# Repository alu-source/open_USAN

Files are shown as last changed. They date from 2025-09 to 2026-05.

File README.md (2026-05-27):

## Summary

1. Overview
2. Build instructions
3. Testing and validation 

## 1. Overview
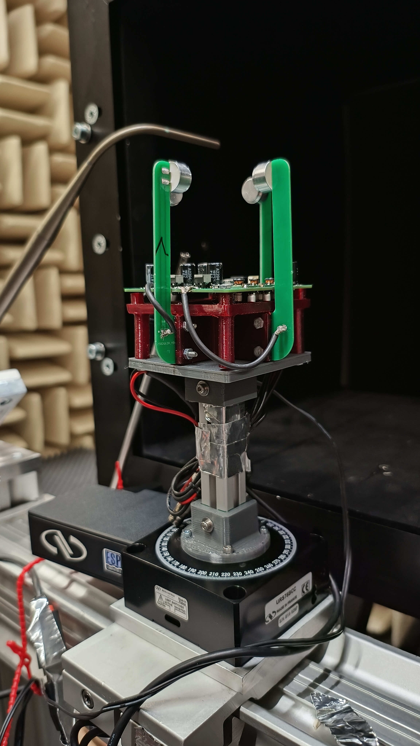
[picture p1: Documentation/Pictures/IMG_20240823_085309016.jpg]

The goal of this project was to create a low cost small scale 2D ultrasonic anenomter. The resulting solution is based on a STM32F4 microcontroller and uses off the shelf electrical components with a cost of around 100€, and offers multiple IO options for data output, a USB interface, a dual-channel analog output, and a synchronization signal input. The sensor can be configured with various parameters and a maximum measurement frequency of 100 Hz can be achieved.
A detailed explanation of the working principle and the technique used can be found in my <a href="/Documentation/Bachelor_thesis.pdf" target="_blank">thesis</a>. 
<br/><br/>
A brief explanation:

The speed of sound and the airspeed are calculated with the help of two ultrasound transmissions in opposite directions, the mean measured speed for both transmissions is the speed of sound and the difference to the mean is the airspeed.

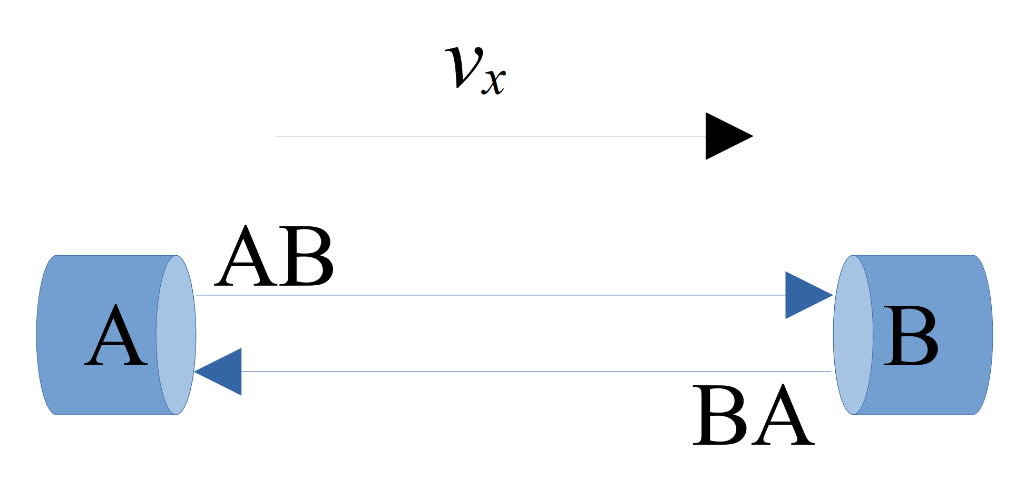
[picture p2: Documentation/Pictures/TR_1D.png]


To accurately calculate the speed of the transmissions, the time of flight (ToF) between transmission and reception must be accurately measured, which requires some neat digital signal processing.
The sensor can be used and configured via serial terminal, all commands and expected behaviour are given in the manual.

## 2. Build instructions
### Hardware
KiCad has been used for the PCB design, the design files and a production-ready export can be found in the Hardware folder.
The PCB can be manufactured by most common PCB manufacturing services such as JLCPCB or Aisler. There are two different types of PCB, a two layer PCB for mounting the transceivers and a four layer PCB for the main board. All components can be soldered by hand, although reflow soldering (using a hot plate or hot air) is highly recommended.
Most components are available from Mouser. The resistors should be 1% accurate and the ceramic capacitors should have a minimum nominal voltage rating of 24V.

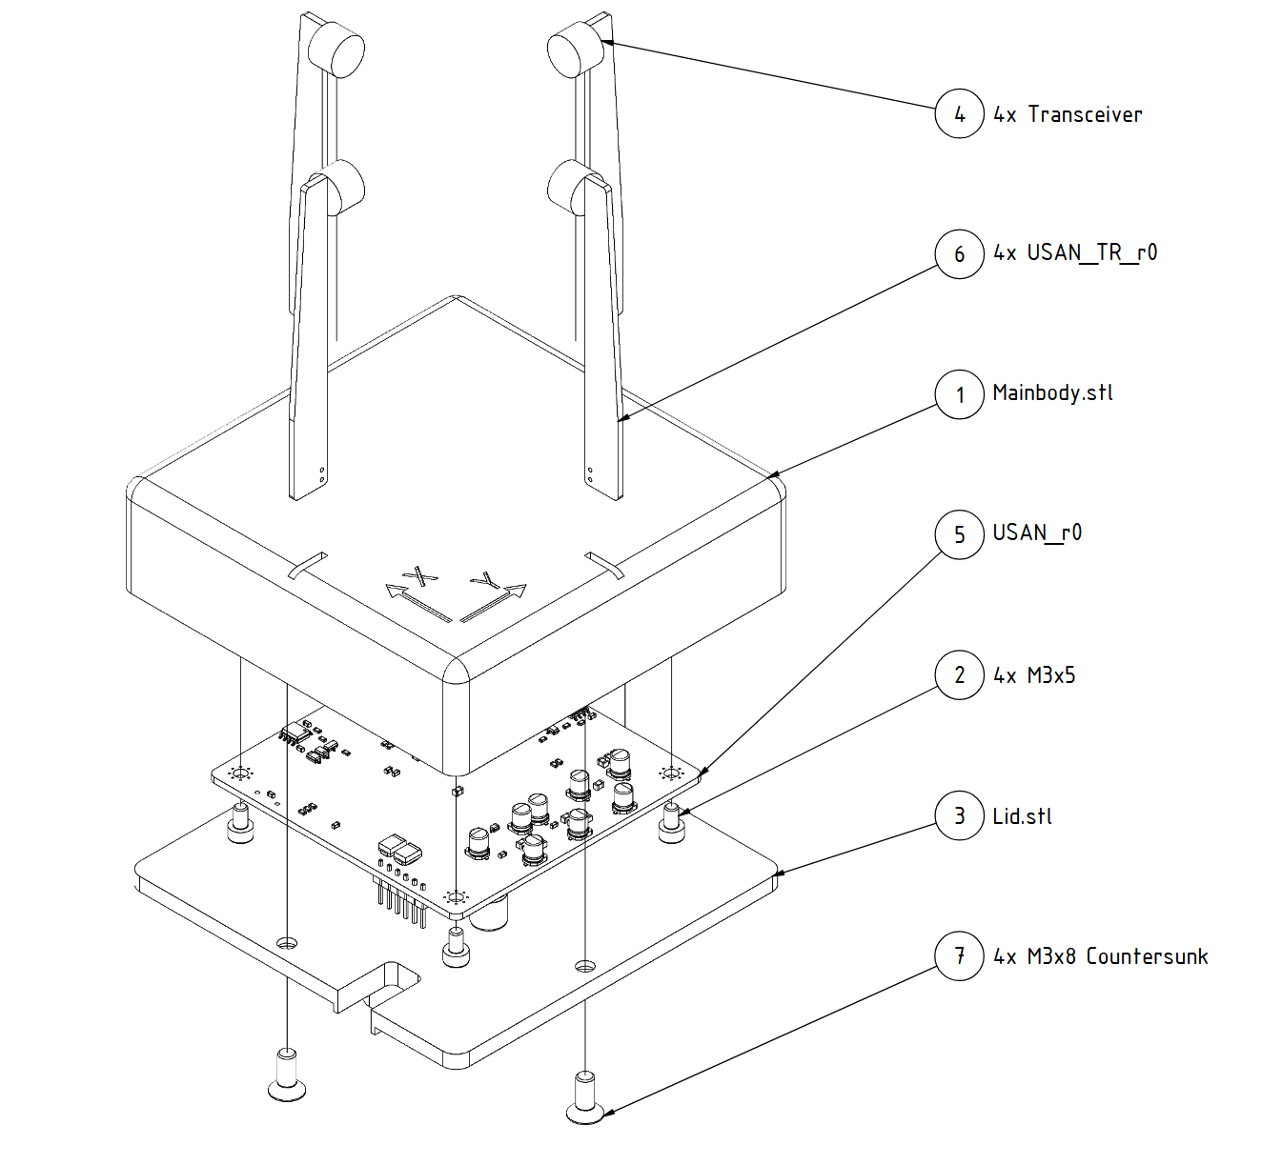
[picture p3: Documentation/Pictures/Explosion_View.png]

The other part of the hardware consists of 3D printed parts and M3 screws.
The arms are glued into the body to create a watertight connection, an epoxy glue should be used. 

### Software
The software devlopment was done in Segger embeded studio the files can be found in the Software folder.
Further configuartion parameters can be set in the sensor_config.h file.
This makes it possible to change the transceiver or to modify the geometry of the sensor.

Using the USB interface, different runmodes an trigger/sample times can be configured, for more information look in to the [manual](https://github.com/alu-source/open-USAN/blob/main/Documentation/Manual/Ultrasonic%20Anemometer%20Reference%20Manual.docx).

## 3. Testing and Validation

Testing and validation was carried out in a wind tunnel capable of generating air speeds of up to 45 m/s.
A prantle tube and a Dantec high pression anemometer were used for velocity measurements.

In the first test, a velocity deficit was detected near the transceiver mounting location due to transceiver blockage, as shown below. 

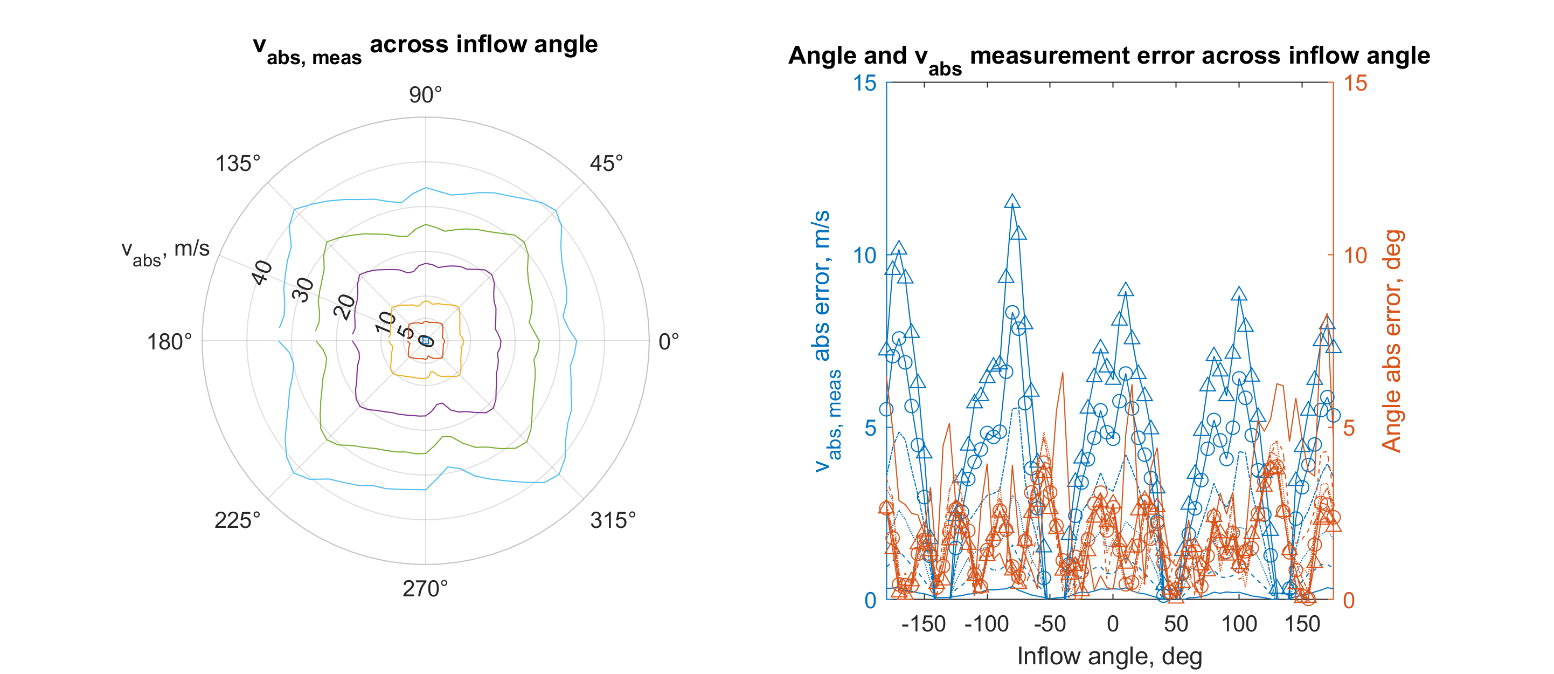
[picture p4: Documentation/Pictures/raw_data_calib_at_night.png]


The left plot shows the measured velocity magnetude and the right plot shows the measurement error of magnitude and angle over the inflow angle. 

In order to counteract this phenomenon, calibration was carried out at various inflow angle and air speeds. 
Each sensor has a slightly different optimum calibration, the data includes an averaged calibration for the sensor which does not give the best sensor performance but eliminates the need to perform a calibration.
A semi-automated [skript] ("/2D-US-Calibration/Skript/Sensor_calibration_and_validation.m") was developed and tested to collect the raw data required for calibration. After calibration, a validation measurement was performed. 
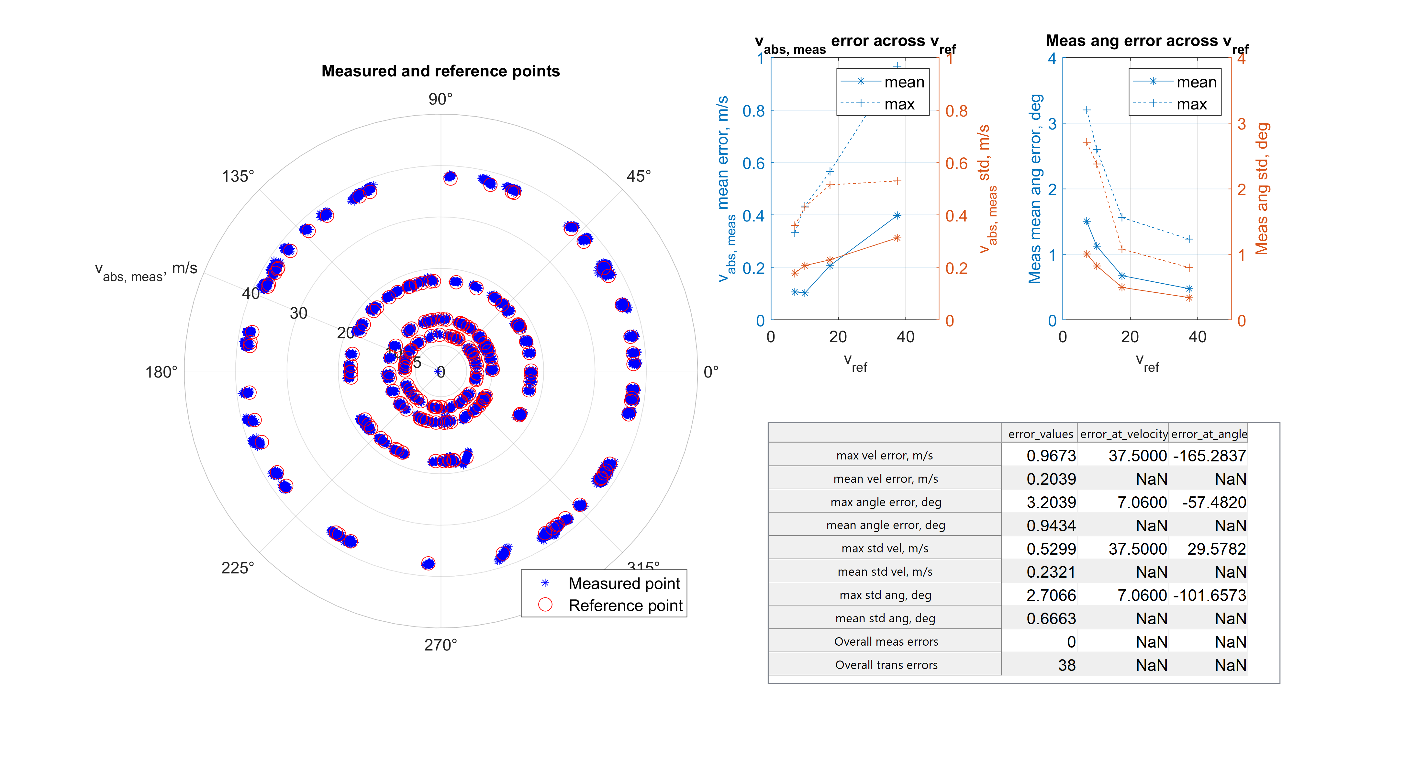
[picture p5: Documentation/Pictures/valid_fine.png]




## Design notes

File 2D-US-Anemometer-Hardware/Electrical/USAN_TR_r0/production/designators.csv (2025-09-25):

G***:1
J1:1
LS1:1

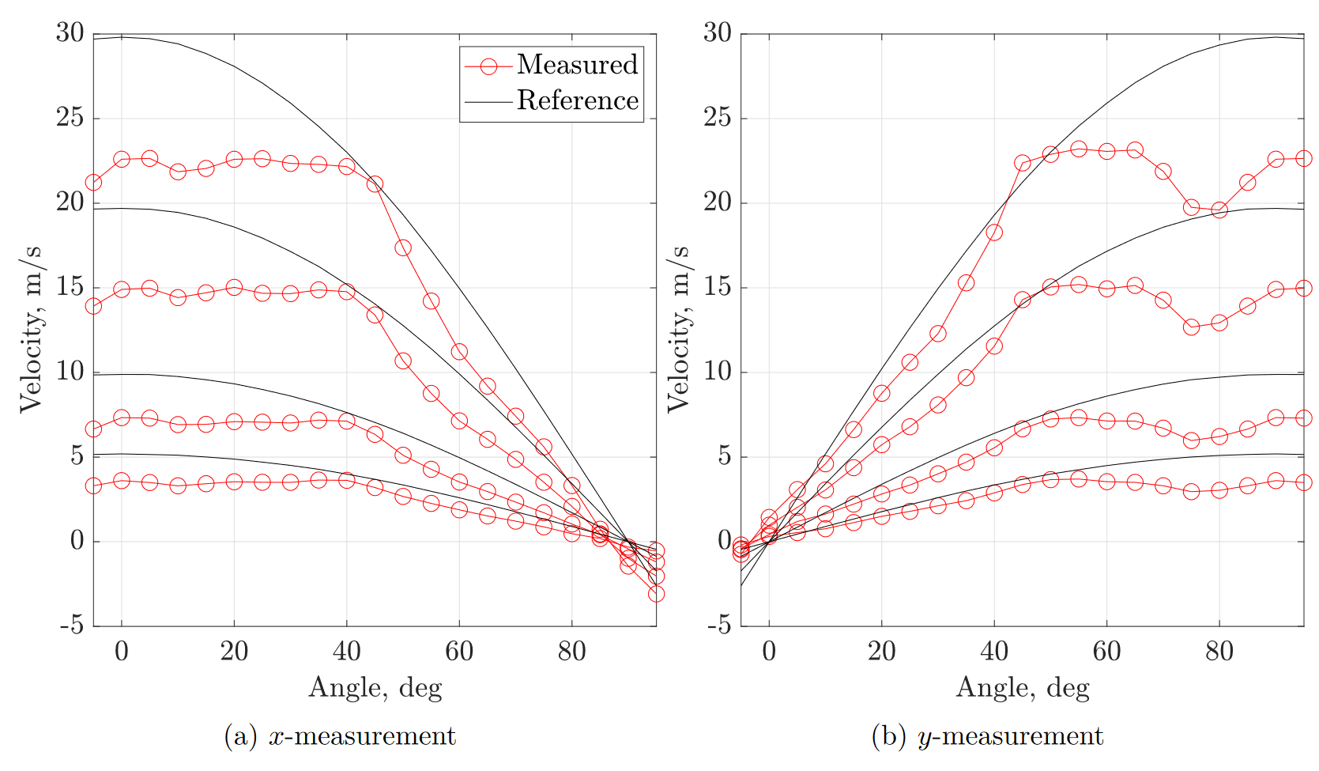
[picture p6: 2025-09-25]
Documentation/Pictures/Velocity_deficit.png

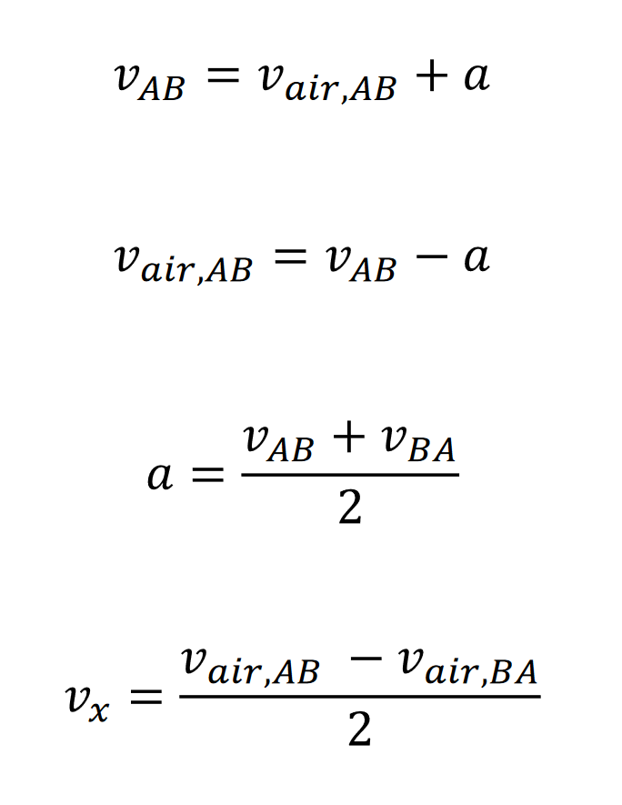
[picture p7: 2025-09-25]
Documentation/Pictures/formulas.png

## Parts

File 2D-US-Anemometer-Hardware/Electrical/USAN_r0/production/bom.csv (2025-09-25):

Designator | Footprint | Quantity | Value | LCSC Part #
C1, C28, C6, C67 | 0805 | 4 | 22u
C10, C11, C12, C13, C2, C86, C89, C9 | CP_Elec_4x5.4 | 8 | 10u, 35V
C14 | CP_Elec_8x10 | 1 | 220uF, 35V
C15, C27, C33, C38, C39, C43, C46, C47, C49, C50, C53, C55, C56, C57, C59, C60, C61, C63, C64, C65, C75, C76, C77, C78 | 0603 | 24 | 1u
C16, C22, C44, C45, C69, C70, C85 | 0805 | 7 | 4u7
C17, C20 | 0805 | 2 | 4u7, 25V
C18, C19, C83, C84 | 0603 | 4 | 100n, 25V
C21, C23, C26, C34, C35, C36, C37, C40, C41, C42, C51, C52, C79, C80, C81 | 0603 | 15 | 100n
C29, C30 | 0603 | 2 | 47p
C31, C32 | 0603 | 2 | 2u2
C4, C82, C88, C92 | 1206 | 4 | C3216X5R1H106K160AB
C48, C54, C58, C62 | CP_Elec_8x6.2 | 4 | EEEFK1C221P
C66 | 0805 | 1 | DNP (22u)
C7, C91 | 0805 | 2 | 10u, 25V
C71, C72, C73, C74 | 0603 | 4 | 1u
C87 | 0805 | 1 | 10u
D1 | D_SMB | 1 | SMBJ24A
D10, D11, D12, D13, D14, D15, D16, D17, D18, D19, D4, D5, D6, D7, D8, D9 | D_SOD-123 | 16 | BAV20W
D2, D20, D3 | 0603 | 3 | LED Blue
D21 | D_SOD-523 | 1 | ESD5Z5.0T1G
D22, D23 | D_SMB | 2 | SMBJ10CA-E3/52
D25 | D_SOD-323 | 1 | BAT54WS-7-F
F1 | 1210 | 1 | SMD1210B020TF
FB1 | 0805 | 1 | MLZ2012N100LT000
IC1, IC2 | SOIC127P600X175-8N | 2 | ICL7660ACBAZA
IC3 | SOP65P640X120-25N | 1 | AD5732AREZ
IC4 | SOT95P280X145-6N | 1 | REF3425TIDBVR
IC5 | SOIC127P600X175-8N | 1 | DNP (IS66WVS4M8BLL-104NLI-TR)
ID1, T_-12V1, T_-5V1, T_12V1, T_24V1, T_3V3, T_5V1, T_Analog1, T_Analog2, T_Analog3, T_Analog4, T_DAC_A1, T_DAC_B1, T_GND1, T_GND2, T_GND3, T_GND4, T_GND5, T_PC1, T_PC2, T_PC3, T_PE10, T_PE7, T_PE8, T_PE9, T_RX1, T_TR_A1, T_TX1, T_VBUS1, T_V_ADJ1, T_V_MCU1, T_V_ref1 | TestPoint_Pad_D1.5mm | 32 | TestPoint
IN1 | PinHeader_1x06_P2.54mm_Vertical | 1 | DNP (Conn_01x06)
J1 | USB_Mini-B_AdamTech_MUSB-B5-S-VT-TSMT-1_SMD_Vertical | 1 | MUSB-B5-S-VT-TSMT-T/R
J3 | 501331-0407 | 1 | 501331-0407
Q1, Q10, Q11, Q2, Q4, Q5, Q7, Q8 | SOT-23-3 | 8 | SI2300DS
R1, R19, R20, R29, R30, R43, R44, R57, R58 | 0603 | 9 | 33k
R10, R32, R46, R60 | 0603 | 4 | 10k
R11, R33, R47, R61 | 0603 | 4 | 1.5k
R12, R14, R16, R22, R24, R36, R50, R66 | 0603 | 8 | 47k
R13 | 0603 | 1 | 20.5k
R15, R23, R37, R51 | 0603 | 4 | 6.2k
R17, R27, R41, R55 | 0603 | 4 | 100k
R18 | 0603 | 1 | 11.5k
R2 | 0603 | 1 | 4k7
R21, R26, R35, R4, R40, R49, R54, R9 | 0603 | 8 | 330R
R25, R3, R39, R53, R75, R76, R77, R78 | 0603 | 8 | 120R
R28 | 0603 | 1 | 4.3k
R31, R34 | 0805 | 2 | 0R
R5, R6 | 0603 | 2 | 27R
R68, R69, R7, R70, R71, R8 | 0603 | 6 | 1k
R72, R73, R74 | 0603 | 3 | DNP (27)
T1, T2, T3, T4 | B78416A2232A003 | 4 | B78416A2232A003
U1 | QFN-20-1EP_4x4mm_P0.5mm_EP2.5x2.5mm | 1 | FT231XQ
U2 | LQFP-100_14x14mm_P0.5mm | 1 | STM32F469VGTx
U3, U4, U5, U6 | SOIC-8_3.9x4.9mm_P1.27mm | 4 | TS912ID
V_ADJ1, V_ADJ2, V_ADJ3, V_ADJ4 | LMZM23600SILT | 4 | LMZM23600SILR
Y1 | ECS2520MV250BNTR | 1 | ECS-2520MV-160-CN-TR

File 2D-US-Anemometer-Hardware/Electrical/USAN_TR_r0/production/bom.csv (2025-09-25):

Designator | Footprint | Quantity | Value | LCSC Part #
J1 | PinSocket_1x02_P2.54mm_Vertical | 1 | Conn_01x02
LS1 | US_Solderpad_2 | 1 | Speaker_Ultrasound_2

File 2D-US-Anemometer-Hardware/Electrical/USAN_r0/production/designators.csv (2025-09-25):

C1:1
C10:1
C11:1
C12:1
C13:1
C14:1
C15:1
C16:1
C17:1
C18:1
C19:1
C2:1
C20:1
C21:1
C22:1
C23:1
C24:1
C25:1
C26:1
C27:1
C28:1
C29:1
C30:1
C31:1
C32:1
C33:1
C34:1
C35:1
C36:1
C37:1
C38:1
C39:1
C4:1
C40:1
C41:1
C42:1
C43:1
C44:1
C45:1
C46:1
C47:1
C48:1
C49:1
C5:1
C50:1
C51:1
C52:1
C53:1
C54:1
C55:1
C56:1
C57:1
C58:1
C59:1
C6:1
C60:1
C61:1
C62:1
C63:1
C64:1
C65:1
C66:1
C67:1
C68:1
C69:1
C7:1
C70:1
C71:1
C72:1
C73:1
C74:1
C75:1
C76:1
C77:1
C78:1
C79:1
C80:1
C81:1
C82:1
C83:1
C84:1
C85:1
C86:1
C87:1
C88:1
C89:1
C9:1
C90:1
C91:1
C92:1
C93:1
D1:1
D10:1
D11:1
D12:1
D13:1
D14:1
D15:1
D16:1
D17:1
D18:1
D19:1
D2:1
D20:1
D21:1
D22:1
D23:1
D25:1
D3:1
D4:1
D5:1
D6:1
D7:1
D8:1
D9:1
DAC_UP1:1
F1:1
FB1:1
G***:3
GND_CONN1:1
H1:1
H2:1
H3:1
H4:1
IC1:1
IC2:1
IC3:1
IC4:1
IC5:1
ID1:1
IN1:1
J1:1
J3:1
JP1:1
JP2:1
LS1:1
LS2:1
LS3:1
LS4:1
Q1:1
Q10:1
Q11:1
Q2:1
Q4:1
Q5:1
Q7:1
Q8:1
R1:1
R10:1
R11:1
R12:1
R13:1
R14:1
R15:1
R16:1
R17:1
R18:1
R19:1
R2:1
R20:1
R21:1
R22:1
R23:1
R24:1
R25:1
R26:1
R27:1
R28:1
R29:1
R3:1
R30:1
R31:1
R32:1
R33:1
R34:1
R35:1
R36:1
R37:1
R39:1
R4:1
R40:1
R41:1
R43:1
R44:1
R46:1
R47:1
R49:1
R5:1
R50:1
R51:1
R53:1
R54:1
R55:1
R57:1
R58:1
R6:1
R60:1
R61:1
R66:1
R68:1
R69:1
R7:1
R70:1
R71:1
R72:1
R73:1
R74:1
R75:1
R76:1
R77:1
R78:1
R8:1
R9:1
SWD_JMP1:1
T1:1
T2:1
T3:1
T4:1
T_-12V1:1
T_-5V1:1
T_12V1:1
T_24V1:1
T_3V3:1
T_5V1:1
T_Analog1:1
T_Analog2:1
T_Analog3:1
T_Analog4:1
T_DAC_A1:1
T_DAC_B1:1
T_GND1:1
T_GND2:1
T_GND3:1
T_GND4:1
T_GND5:1
T_PC1:1
T_PC2:1
T_PC3:1
T_PE10:1
T_PE7:1
T_PE8:1
T_PE9:1
T_RX1:1
T_TR_A1:1
T_TX1:1
T_VBUS1:1
T_V_ADJ1:1
T_V_MCU1:1
T_V_ref1:1
U1:1
U2:1
U3:1
U4:1
U5:1
U6:1
V_ADJ1:1
V_ADJ2:1
V_ADJ3:1
V_ADJ4:1
Y1:1

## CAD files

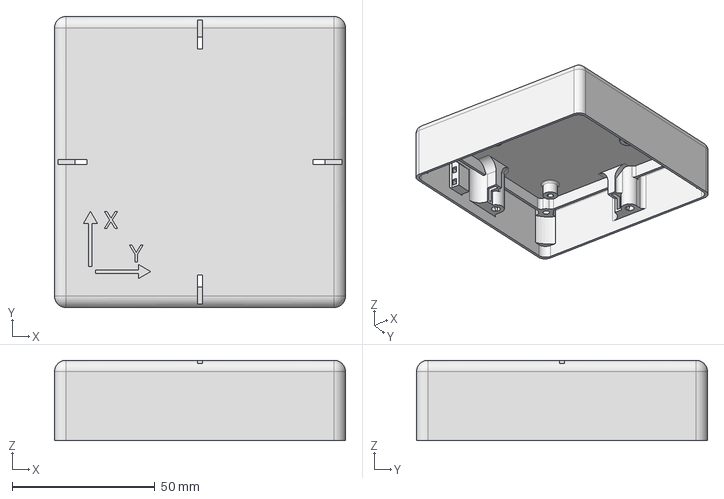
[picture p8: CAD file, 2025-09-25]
2D-US-Anemometer-Hardware/CAD/Exports/Mainbody.stp
102.0 x 102.0 x 28.2 mm

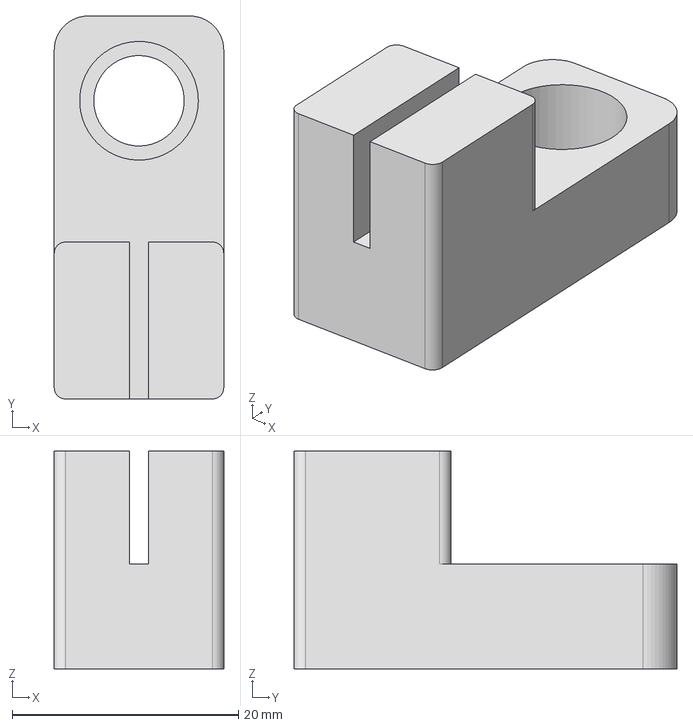
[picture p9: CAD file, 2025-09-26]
2D-US-Anemometer-Hardware/CAD/Exports/Solder_aid.stp
15.0 x 33.9 x 19.2 mm

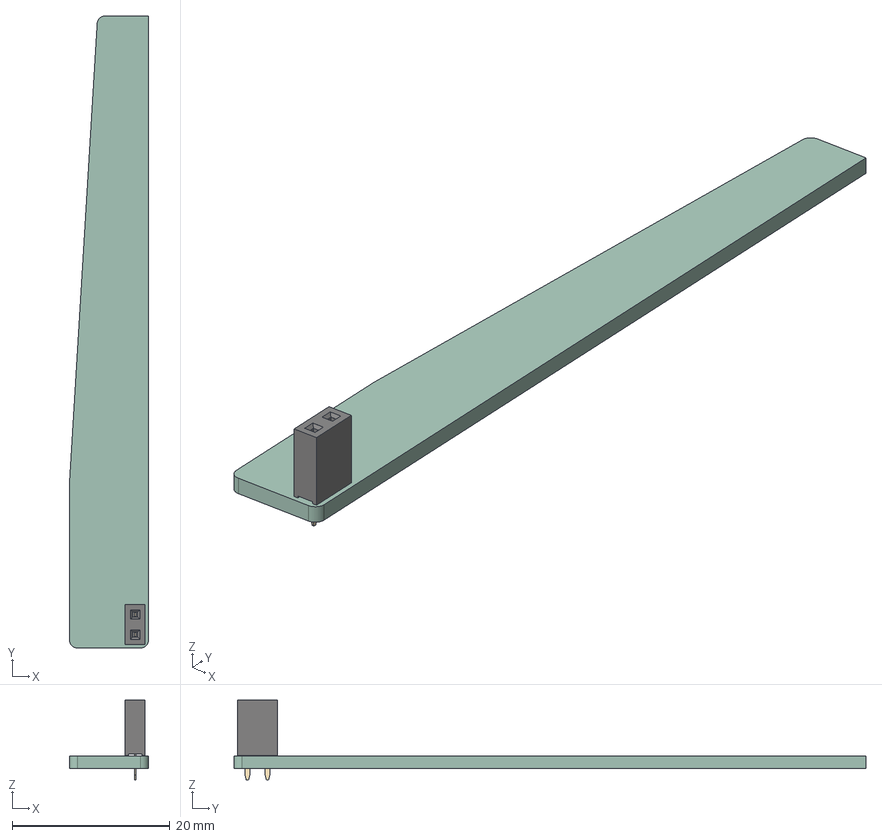
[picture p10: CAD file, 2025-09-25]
2D-US-Anemometer-Hardware/CAD/USAN_TR_r0.step
10.0 x 80.0 x 10.1 mm
PinSocket_1x02_P254mm_Vertical
USAN_TR_r0_PCB

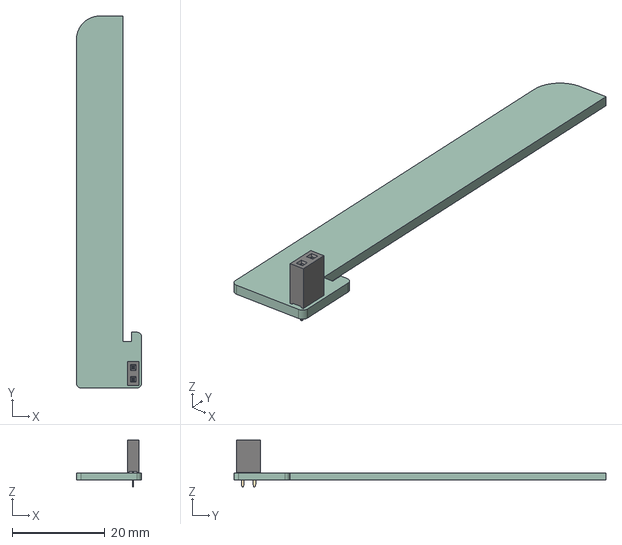
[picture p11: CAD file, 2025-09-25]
2D-US-Anemometer-Hardware/Electrical/USAN_TR_r0/USAN_TR_r0.step
14.0 x 80.0 x 10.1 mm
PinSocket_1x02_P254mm_Vertical
USAN_TR_r0_PCB

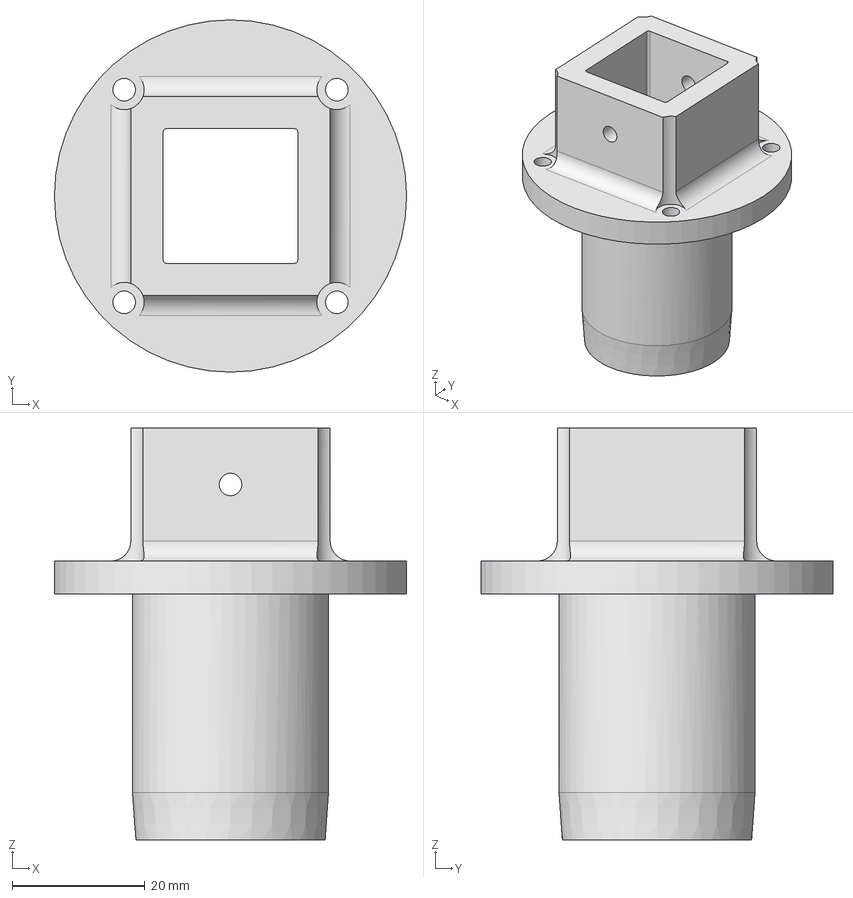
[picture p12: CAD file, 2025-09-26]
2D-US-Anemometer-Hardware/CAD/Exports/URS75_mount.stp
53.0 x 53.0 x 62.0 mm

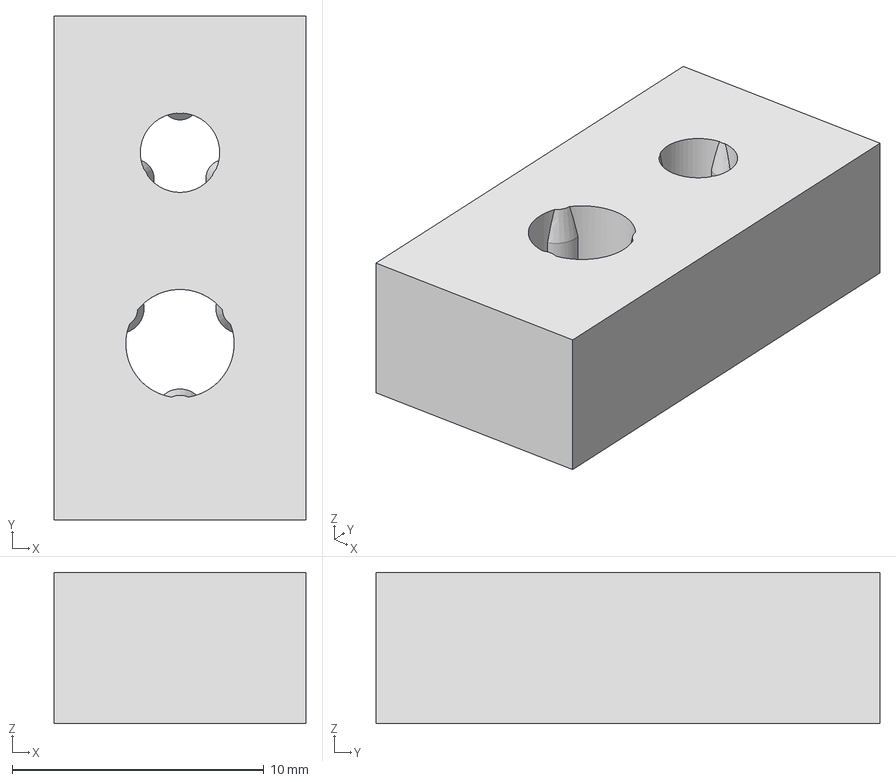
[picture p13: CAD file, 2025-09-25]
2D-US-Anemometer-Hardware/CAD/Exports/Tolerance_test.stp
10.0 x 20.0 x 6.00 mm

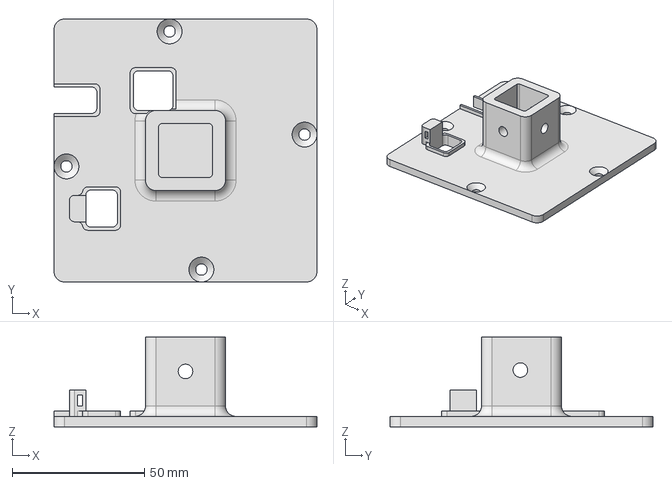
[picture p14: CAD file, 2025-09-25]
2D-US-Anemometer-Hardware/CAD/Exports/Lid_uart.stp
99.4 x 99.4 x 34.0 mm

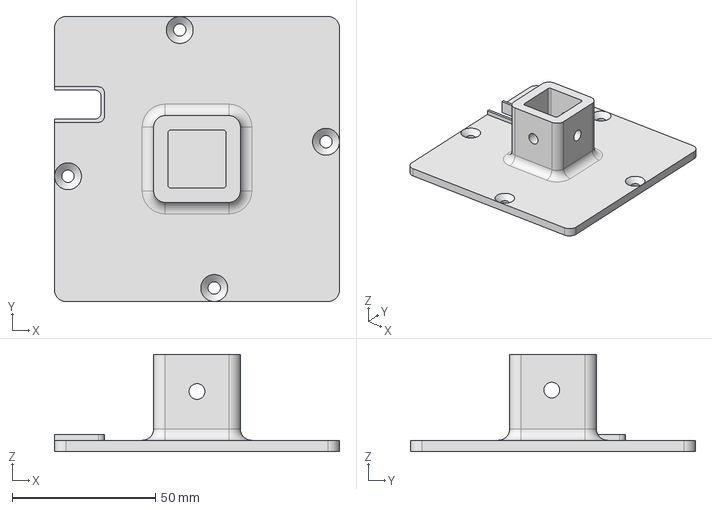
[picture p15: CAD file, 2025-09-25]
2D-US-Anemometer-Hardware/CAD/Exports/Lid.stp
99.4 x 99.4 x 34.0 mm

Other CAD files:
2D-US-Anemometer-Hardware/CAD/Exports/Lid.stl
2D-US-Anemometer-Hardware/CAD/Exports/Lid_uart.stl
2D-US-Anemometer-Hardware/CAD/Exports/Mainbody.stl
2D-US-Anemometer-Hardware/CAD/Exports/Solder_aid.stl
2D-US-Anemometer-Hardware/CAD/Exports/Solderaid.stp
2D-US-Anemometer-Hardware/CAD/Exports/URS75_mount.stl

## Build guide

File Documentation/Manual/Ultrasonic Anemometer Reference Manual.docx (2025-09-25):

# Ultrasonic Anemometer Reference Manual

Features

- Measurement of airspeeds up to 50 m/s
  - Between 50 m/s and 60 m/s the sensor returns 50 m/s. After 60 m/s the sensor returns nonsensical data!
- Analog or digital output
- Triggered or automatic measurement mode
- Averaged or double shot measurement
- Sub measurement frequency of up to 250 Hz
- Maximum average time 1s
- USB-Serial interface
- Low power consumption 16 -24 V, 100 mA

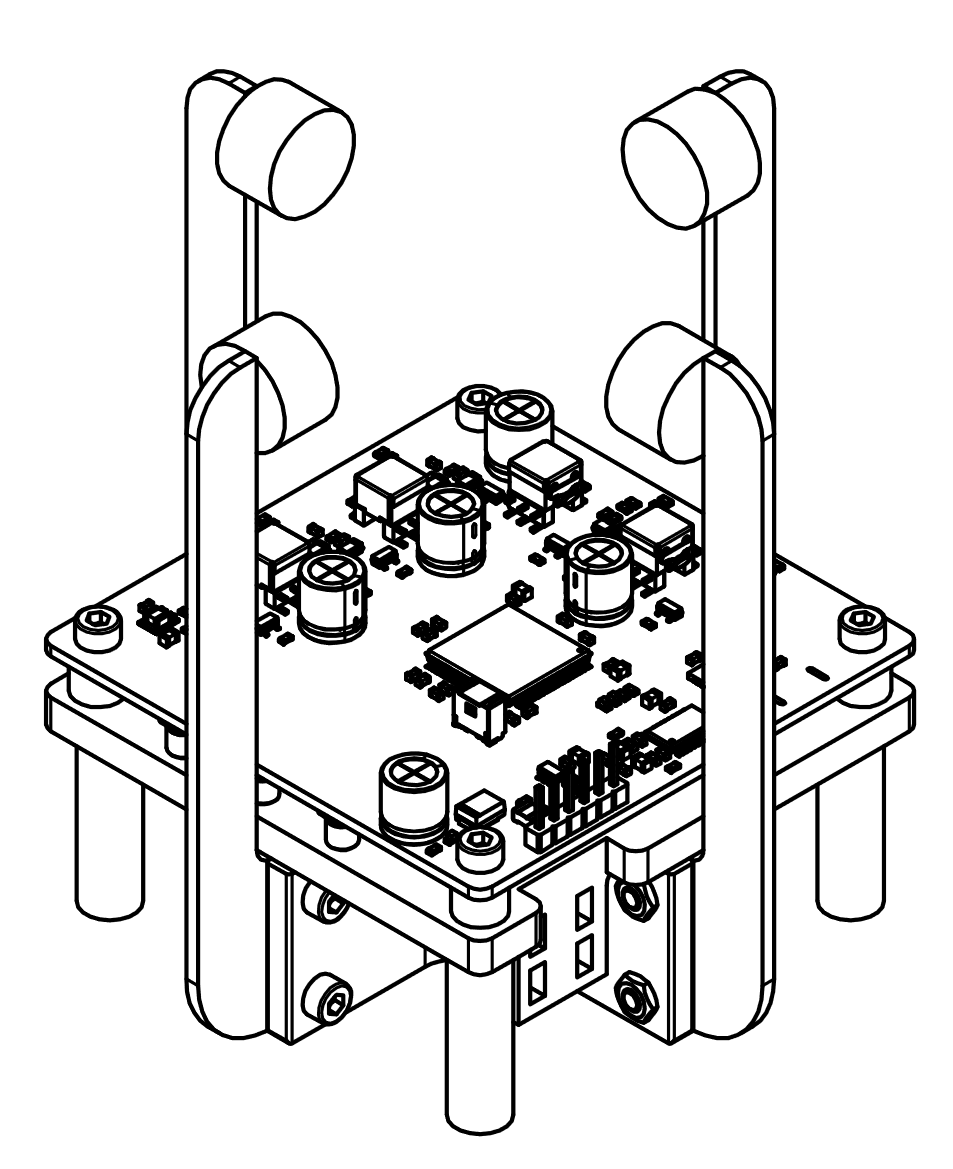
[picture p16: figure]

PCB overview:

PCB first steps:

- Jumper besides SWD connector set to the arrow position
- All other jumpers must be set to the position nearest the board edge
- Solder the analog ground jumper on the other PCB side
- Check the resistances before applying power
  - GND –> -12 V
  - GND –> -5 V
  - GND –> 3.3 V
  - GND –> 5 V
  - GND –> V_drive
  - GND –> 12 V
  - Transceivers pad terminals towards each other ~ 23 Ohm
  - A0 -> VCC
  - A0 -> A1 ~ 33 kOhm
  - A1 -> A2 ~ 33 kOhm
  - A2 -> A3 ~ 33 kOhm
  - A3 -> A4 ~ 33 kOhm
- Connect to lab bench power supply at 24V and current limit of 100mA
  - Current should be lower than 40mA in idle
  - Power LED should be on, if the power LED is off and current near zero the PTC fuse has been triggered
- Check all voltages:
  - -12 V, 12 V
  - -5 V, 5 V
  - 3.3 V
  - V_drive ~ 8V

The sensors serial interface has a baud rate of 1Mbaud and the following commands:

Command (Name) | Options [Var_type (Var_name, unit), …] | Return
-h (Help) | - | List of commands
-t (Trigger) | [ f (f_trigger, Hz), f (d_trigger, %)], f_trigger -> Max. external trigger frequency: f_trigger = 0 -> trigger deactivated, f_trigger < 100 Hz, d_trigger -> Duty cycle of the measurement, d_trigger = 1 -> double shot mode, d_trigger <= 100% | Actual measurement parameters
-s (Status) | - | Returns all current settings / parameters
-e (Exit) | - | Confirmation
-w (Write to EEPROM) | - | Saves new config to EEPROM
-n (Zero measurement) | [f (temp, °C)], must be taken under no wind speed condition aka in a big box or so. | Returns new t_0 and ref speed of sound
-p (Ping) | | Returns Sensor name and puts out a +9V, 0V, -9V signal on both DAC channels
-c (Calibration mode) | [i (mode)], mode = 0 -> first time enter calibration mode after that return raw measurement mode = 1 -> Get calibration from PC (mode = 2 -> read calibration) mode = 4 -> return raw and corrected value needs a trigger [f32 (raw_x), f32 (raw_y), f32 (corr_x), f32 (corr_y), u32 (crc32)] in binary mode = 11 -> set to normal mode with trigger mode = 12 -> set to free run mode | Returns corrected / uncorrected measurement data
-I (Info) | [c (operation), i (ID)], operation = ? -> get ID of the sensor returns 0xFFFF (65535) if unset operation = ! -> writes ID to sensor, needs confirmation from user, the ID can only be written once ! | Returns ID of the sensor
-a (ASCII mode) | [i (mode)], mode = 0 -> leave ASCII output mode mode = 1 -> enter continuous ASCII output mode = 2 -> one time ASCII output | Only returns error or missing value massage

If an external Trigger is applied the USAN has the following LED error codes:

Description | LED 0 | LED 1 | DAC | Action
Normal behaviour | Flashing with half the trigger frequency | OFF | Voltage between -9.5 V and 9.5 V | All good
EEPROM error or other critical error | Flashing | Flashing | Voltage stepps | Connect to serial interface and restart sensor. Serial interface output will give further instructions
Trigger to early warning | - | ON | - | Trigger was faster than expected, reconfigured measurement with higher trigger frequency can be ignored if it jumps off again
Measurement error | - | ON | - | Sensor has experienced an error while measuring, can be ignored if it jumps off again
Trigger lost warning | Constant | OFF | If in trigger mode both channels Zero other wise valid output | If

The schematic of the software execution is as follows:

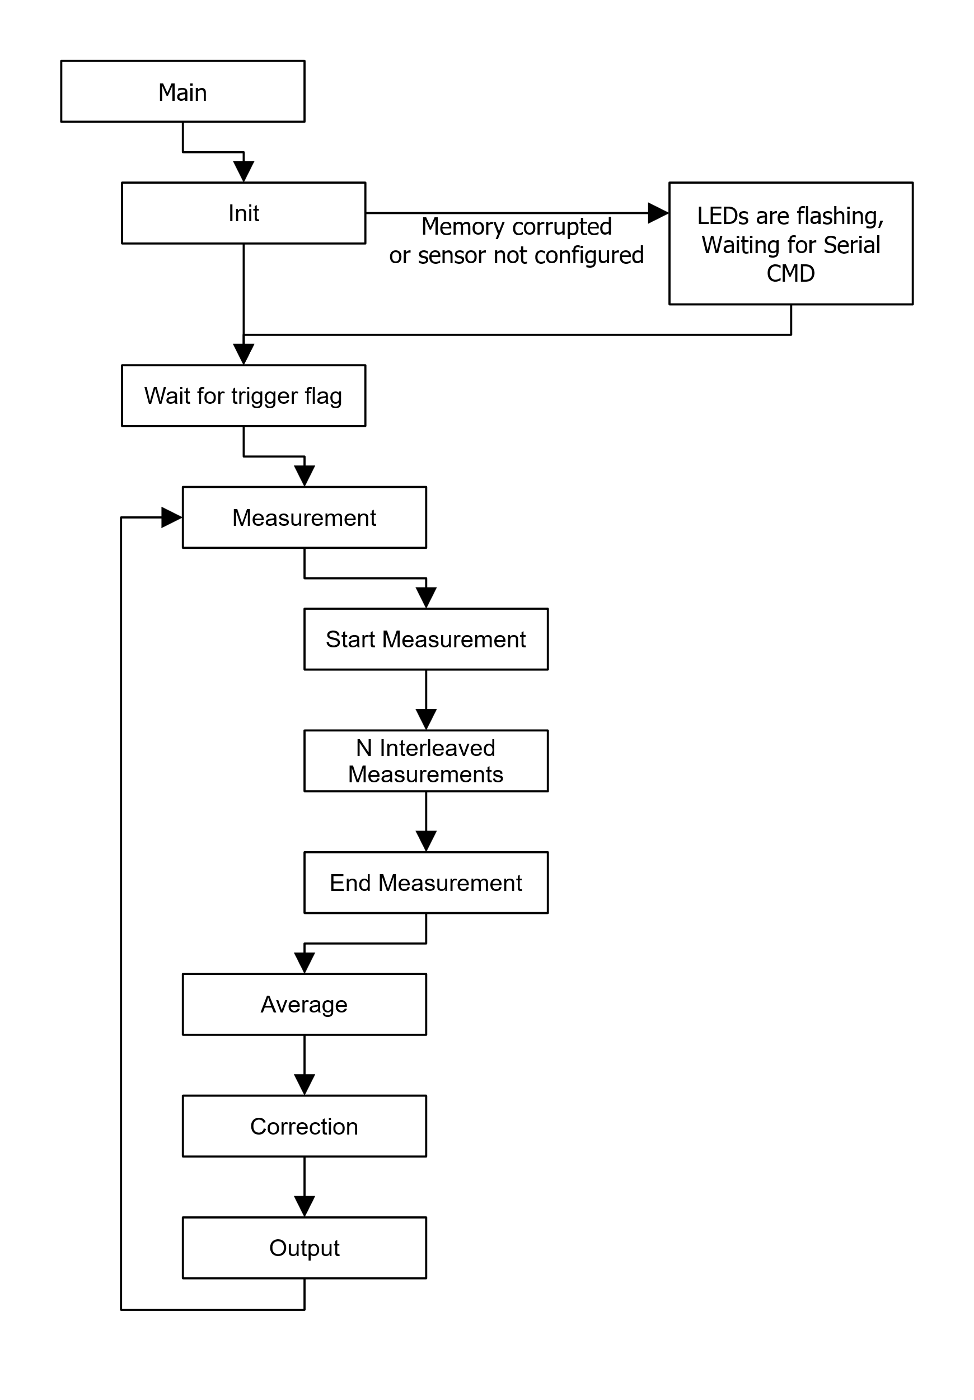
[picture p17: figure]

How to set up a sensor:

Steps:

1. Flash the sensor
2. Self-test the sensor
3. Record the zero measurement
4. Setup the sensor
1. Flash the sensor
  a. Download Segger Embedded Studio for Arm and RISC-V (https://www.segger.com/downloads/embedded-studio/#embeddedstudio)
    i. Version used: 8.14
  b. Downlaod STM32CubeProg (https://www.st.com/en/development-tools/stm32cubeprog.html)
    i. CONTINUE HERE
  c. Start Segger and install the following packages via “Tools” – “Package Manager”
    i. CMSIS 5 CMSIS-CORE Support Package,
    ii. CMSIS 5 CMSIS-DSP Support Package,
    iii. CMSIS 5 Documentation Package
    iv. STMicroelectronics STM32F4xx CPU Support Package
  d. Connect the Flasher (STLINK-V3MINIE) with the board (marked SWD on the PCB) and the PC
  e. Power up the sensor (power LED on)
  f. Open the “2D-Anemometer-Firmware_r0.emProject” with Segger via “File” – >“Open solution”
  g. Press “Play button” to flash program
    i. The sensor can be further configured with “Sensor_config.h” file for different measurements path lengths or sub measurement frequencies
      1. Activate key testing mode, useful if the transceiver model has been changed (KEY_TEST 0 to KEY_TEST 1), testing should be done under the no airspeed condition and takes about 1 h, if to may keys do not pass due to over (>1000) or under (> 20) amplitude errors change to gain accordingly. The sensor logs the progress over the serial output at a baud rate of 1Mbaud. After completing change the default key to the new key (KEY_DEFAULT) in the configuration file.
      2. Change transceiver distance (d_0 in meters), and the ADC sample offset
      3. Change sub measurement frequency (default and max 200Hz), lowering the sub measurement frequency can help at higher airspeeds due to improved signal amplitude
    ii. If needed, rebuild project
2. Zero measurement
  a. Open a serial terminal with for example the Arduino IDE, and a baud rate of 1Mbaud
  b. Must be taken under a zero windspeed condition, and known speed of sound, e.g., in a big enough box (50cmx50cmx50cm) too small boxes lead to bad filter results
  c. The -n command the zero measurement can be started
    i. If errors or warnings occur “Bad match” etc. check transceivers and transceiver voltage V_drive
3. Calibration of the Sensor
  a. Setup:
    i. The sensor is tested on the URS75BCC turn stage following is needed:
      1. USB to RS232 Adapter
      2. SMC 100 motor controller and power supply
      3. URS75BCC and Cabel
      4. Adapter for X95 to URS75BCC, URS75BCC to Item 20x20 (URS75_to_Item20.stl) and sensor mounting plate (Sensor_to_20x20_Item.stl)
    ii. The sensor and a mini-USB cable
    iii. Arduino trigger board if the validation should trigger an outside(external) device (like a dewetron)
    iv. Velocity references
    v. Mounting:
      1. Place the URS75 (Turntable) so that the 0° is normal to the nozzle (points towards the nozzle)
      2. The sensor should be mounted with the x arrow of the coordinate system on PCB is pointing away from the zero-degree mark (in wind direction)
      3. While connecting the cables, special care should be taken to avoid tension or the cable catching on obstacles due to the sensors motion.
      4. Tape the mini-USB cable to the sensor so it can’t move, otherwise the connection to the PC is lost and the calibration has to be restarted!
  b. Start the Calibration using the MATLAB script (“Sensor_calibration_and_validation.m”) and follow the instruction, calibration should take about an hour minutes
4. Setup
  a. With the -t command the trigger must be configured
    i. -t will put the sensor in a triggerless state
    ii. -t 20 100 will put the sensor in mode where it expects a 20 Hz trigger and measures for 100% of the trigger period
  b. Save everything with the -w command!
  c. Press -e to exit, a small overview over the configuration should be shown

Firmware overview:

Main.c -> Start point of application and high-level process

Unittest.c -> Start up and Serial interface code

Measurement.c -> Measurement process

    - Matched_Filter_r0.c -> Applies matched filter and extracts peaks
    - Filter_Fusion_r0.c -> Combines two matched filters into a 1D measurement
    - Fusion_eval_r0.c -> Combines two 1D measurements into a 2D measurement
    - Correction.c -> Applxies correction to a 2D measurement
    - Algo_helper.c -> Helper functions for the aforementioned functions

Drivers -> Folder of low drivers

    - DAC_AD5732.c -> Driver and interface code for DAC
    - EEPROM.c -> Uses part of the flash sectors of the MCU to emulate EEPROM and create persistent storage -> Used sectors are deleted from memory-map!
    - Gpio.c -> Gpio drivers
    - OPT.c -> Interface to read and write to one-time programable storage (OPT)
    - Packet_transfer.c -> CRC32 function and old packet_transfer code
    - Shared.c -> Collection of Shared functions and miniscule code
    - Shot.c -> Used to start recordings and unlock the data, if the recording is finished, as well as to generate the gpio patterns for transmission
    - SRAM_IS66.c -> Driver for interfacing with the SPI RAM
    - Uart.c -> non-blocking Serial (UART) driver

Sensor data output:

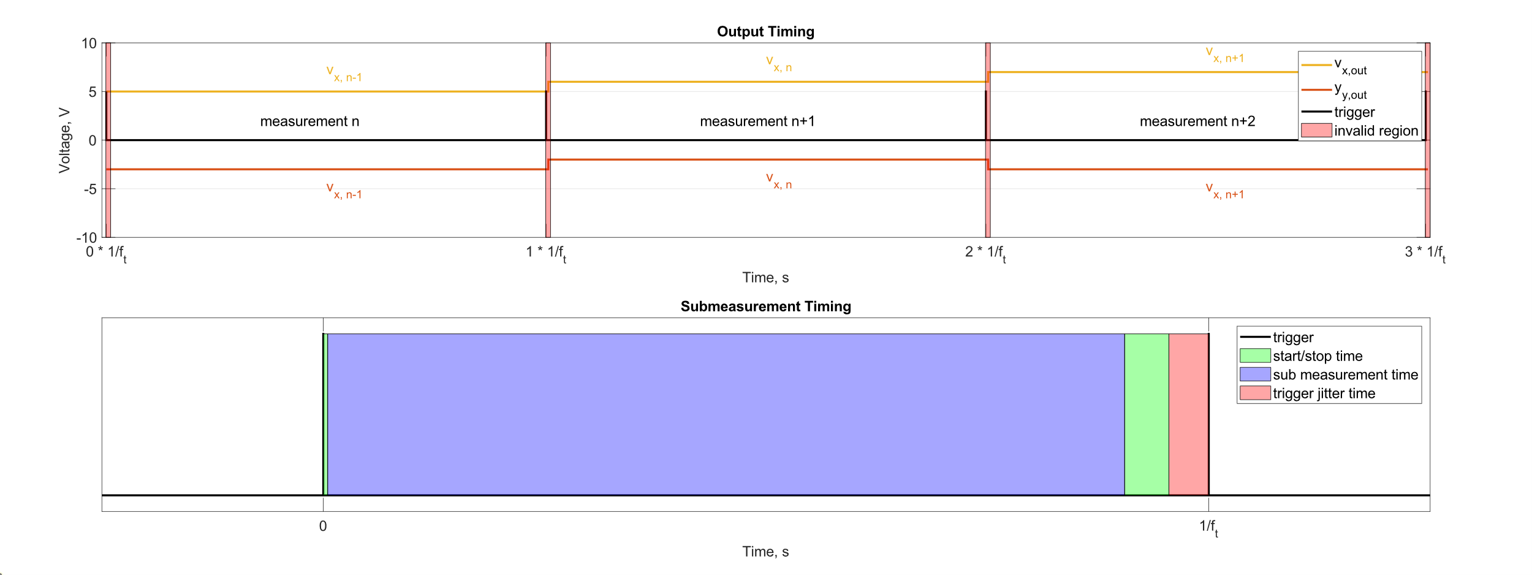
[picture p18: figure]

Output timing:

If the trigger is enabled the output of the sensor is updated on rising edge of trigger signal with the value of the previous measurement. If the trigger is disabled, the output is updated as soon as the measurements is finished. Due to the time needed for the microcontroller to update the DAC and the DAC to reach a steady output state, a non-valid output region does exist. This region can be negated by using an offset to the trigger signal of around 3 ms before and after the trigger but this offset may vary depending on the method used to extract the rising edge form the measurement data.

Sub measurement timing and filtering:

Each sensor measurement consists of a minimum of 2 sub measurements and maximum of 200 sub measurements.

When the trigger is configured, the sensor calculates the time in between trigger events. To compensate for trigger jitter and clock mismatch, a margin is subtracted from this time (trigger jitter time). Furthermore, the time needed to start and stop the measurement is subtracted (start/stop time). The remaining time multiplied with the configured duty cycle is the time available for sub measurements (sub measurement time). The amount of sub measurements is then calculated as the highest amount of sub samples which can be taken (with the sub measurement frequency) in the sub measurement time.

After all measurements are taken, an error and outlier detection is performed, subsequently the remaining measurements are averaged. The outlier detection is performed by filtering for velocity changes over 25 m/s.

In a final step the measurement is corrected with a lookup matrix.

Sensor startup:

When the Sensors powers on a voltage stair is displayed on its analog outputs

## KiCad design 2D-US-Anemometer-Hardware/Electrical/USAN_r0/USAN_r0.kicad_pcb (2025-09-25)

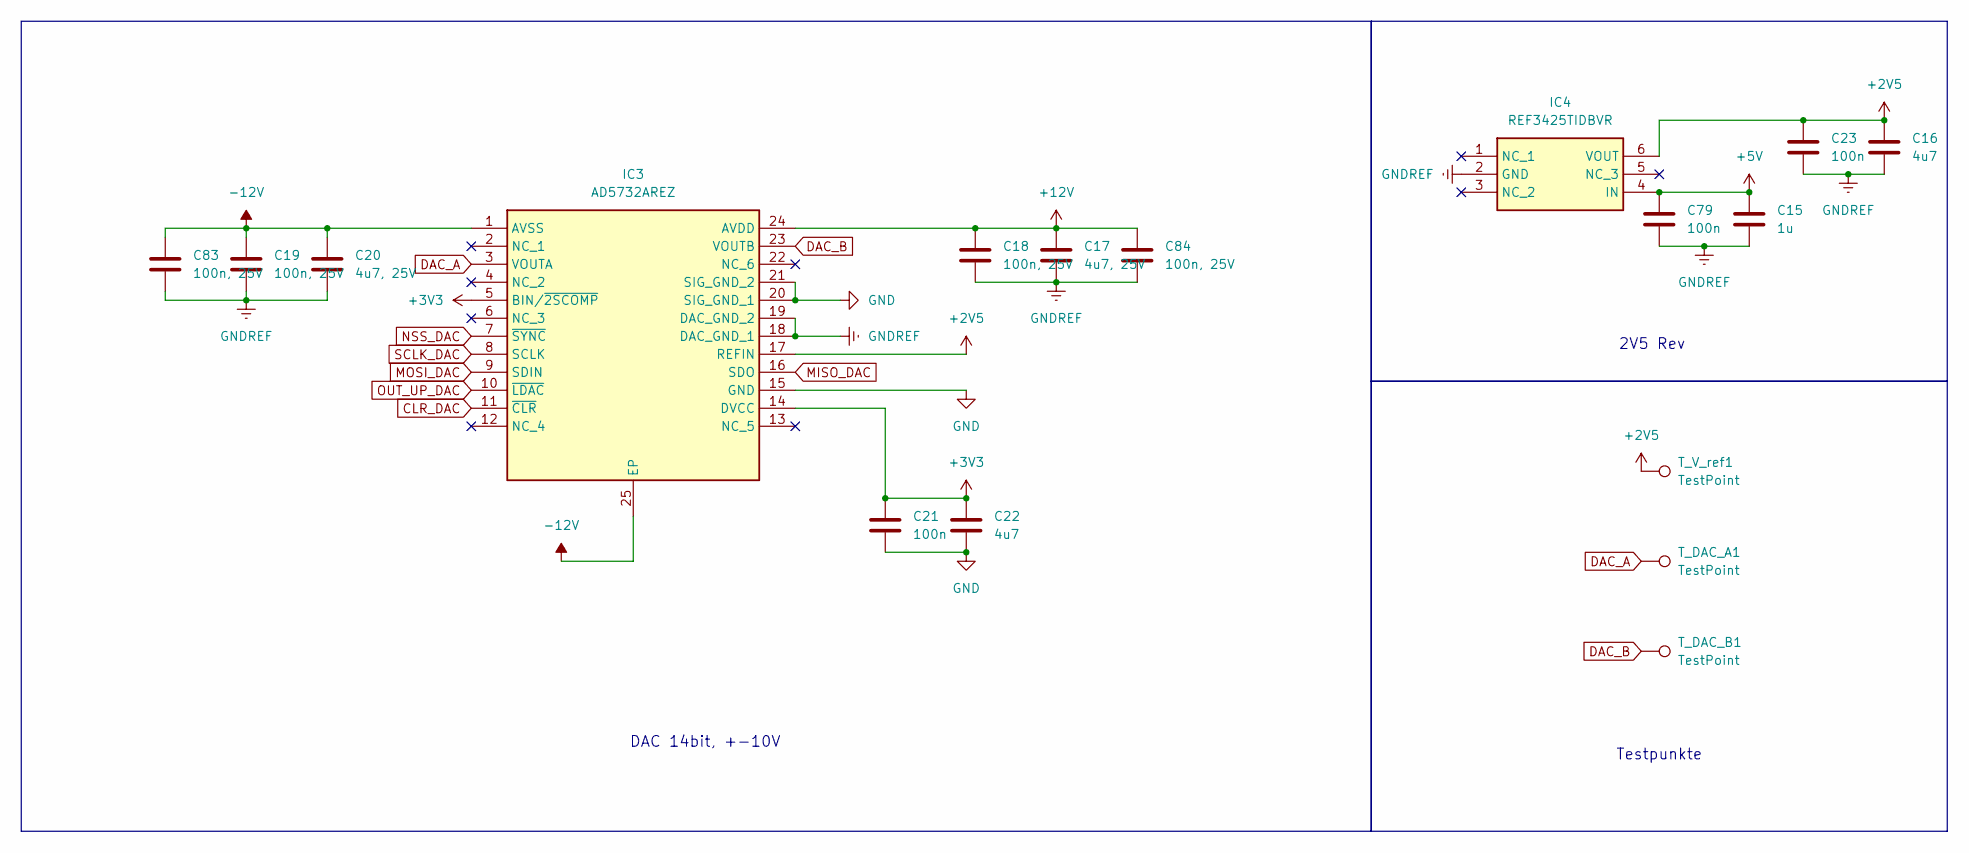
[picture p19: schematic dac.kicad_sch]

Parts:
C15: 1u; C_0603_1608Metric
C16, C22: 4u7; C_0805_2012Metric
C17, C20: 4u7, 25V; C_0805_2012Metric
C18, C19, C83, C84: 100n, 25V; C_0603_1608Metric
C21, C23, C79: 100n; C_0603_1608Metric
IC3: AD5732AREZ; SOP65P640X120-25N; Mouser Part Number 584-AD5732AREZ
IC4: REF3425TIDBVR; SOT95P280X145-6N; Mouser Part Number 595-REF3425TIDBVR
T_DAC_A1: TestPoint; TestPoint_Pad_D1.5mm
T_DAC_B1: TestPoint; TestPoint_Pad_D1.5mm
T_V_ref1: TestPoint; TestPoint_Pad_D1.5mm

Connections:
+2V5: C16.1, C23.1, IC3.17 (REFIN), IC4.6 (VOUT), T_V_ref1.1
+3V3: C21.1, C22.1, IC3.5 (BIN/~2SCOMP), IC3.14 (DVCC); also elsewhere on the board
+5V: C15.1, C79.1, IC4.4 (IN); also elsewhere on the board
+12V: C17.1, C18.1, C84.1, IC3.24 (AVDD); also elsewhere on the board
-12V: C19.1, C20.1, C83.1, IC3.1 (AVSS), IC3.25 (EP); also elsewhere on the board
CLR_DAC: IC3.11 (~CLR); also elsewhere on the board
DAC_A: IC3.3 (VOUTA), T_DAC_A1.1; also elsewhere on the board
DAC_B: IC3.23 (VOUTB), T_DAC_B1.1; also elsewhere on the board
GND: C21.2, C22.2, IC3.15 (GND), IC3.20 (SIG_GND_1), IC3.21 (SIG_GND_2); also elsewhere on the board
GNDREF: C15.2, C16.2, C17.2, C18.2, C19.2, C20.2, C23.2, C79.2, C83.2, C84.2, IC3.18 (DAC_GND_1), IC3.19 (DAC_GND_2), IC4.2 (GND); also elsewhere on the board
MISO_DAC: IC3.16 (SDO); also elsewhere on the board
MOSI_DAC: IC3.9 (SDIN); also elsewhere on the board
NSS_DAC: IC3.7 (~SYNC); also elsewhere on the board
OUT_UP_DAC: IC3.10 (~LDAC); also elsewhere on the board
SCLK_DAC: IC3.8 (SCLK); also elsewhere on the board

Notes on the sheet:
2V5 Rev
DAC 14bit, +-10V
Testpunkte

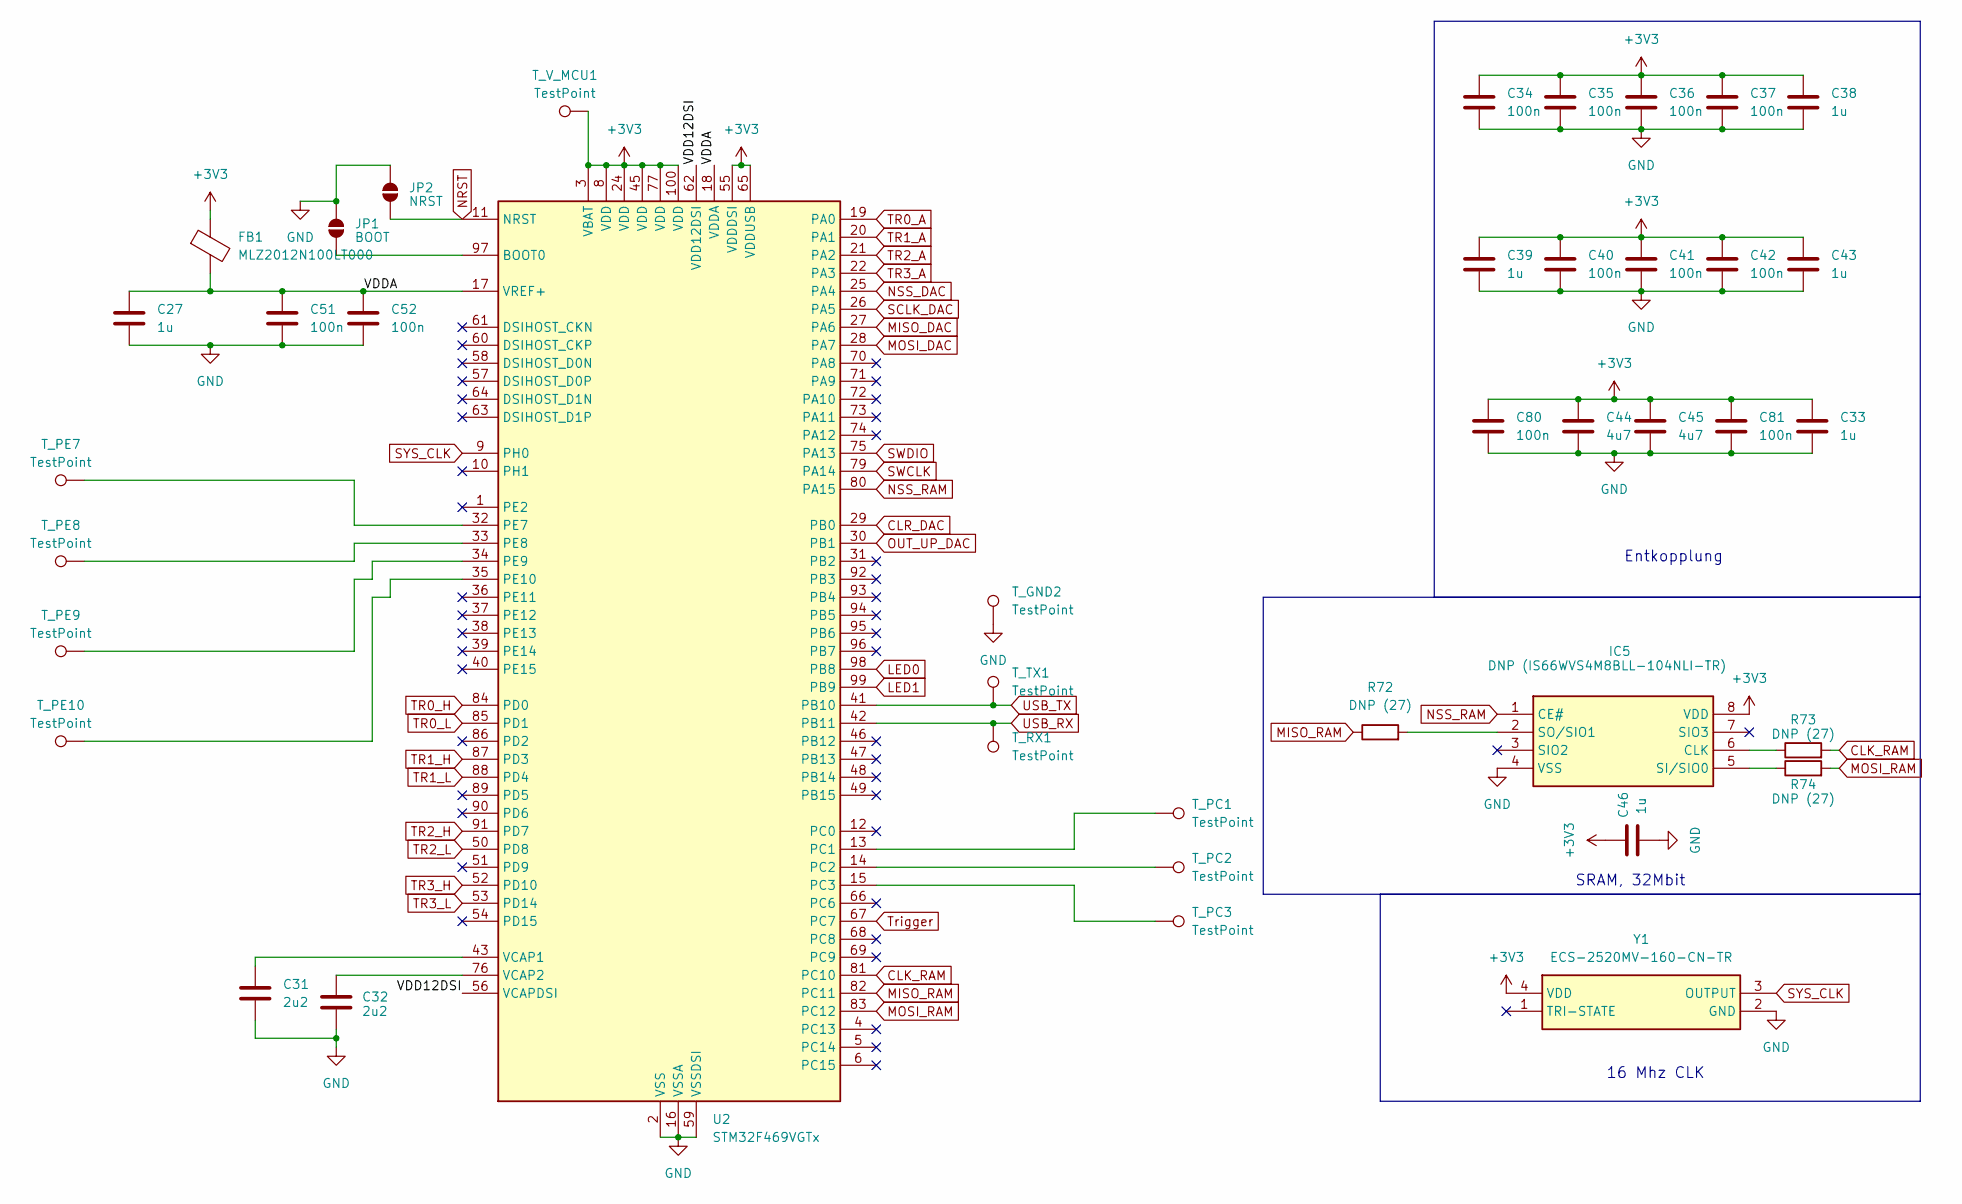
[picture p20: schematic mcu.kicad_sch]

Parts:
C27, C33, C38, C39, C43, C46: 1u; C_0603_1608Metric
C31, C32: 2u2; C_0603_1608Metric
C34, C35, C36, C37, C40, C41, C42, C51, C52, C80, C81: 100n; C_0603_1608Metric
C44, C45: 4u7; C_0805_2012Metric
FB1: MLZ2012N100LT000; L_0805_2012Metric
IC5: DNP (IS66WVS4M8BLL-104NLI-TR); SOIC127P600X175-8N; Mouser Part Number 870-WVS4M8BLL104NLIT
JP1: BOOT; SolderJumper-2_P1.3mm_Open_RoundedPad1.0x1.5mm
JP2: NRST; SolderJumper-2_P1.3mm_Open_RoundedPad1.0x1.5mm
R72, R73, R74: DNP (27); R_0603_1608Metric
T_GND2: TestPoint; TestPoint_Pad_D1.5mm
T_PC1, T_PC2, T_PC3: TestPoint; TestPoint_Pad_D1.5mm
T_PE7, T_PE8, T_PE9, T_PE10: TestPoint; TestPoint_Pad_D1.5mm
T_RX1: TestPoint; TestPoint_Pad_D1.5mm
T_TX1: TestPoint; TestPoint_Pad_D1.5mm
T_V_MCU1: TestPoint; TestPoint_Pad_D1.5mm
U2: STM32F469VGTx; LQFP-100_14x14mm_P0.5mm
Y1: ECS-2520MV-160-CN-TR; ECS2520MV250BNTR; Mouser Part Number 520-2520MV-160-CNT

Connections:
+3V3: C33.1, C34.1, C35.1, C36.1, C37.1, C38.1, C39.1, C40.1, C41.1, C42.1, C43.1, C44.1, C45.1, C46.2, C80.1, C81.1, FB1.1, IC5.8 (VDD), T_V_MCU1.1, U2.3 (VBAT), U2.8 (VDD), U2.24 (VDD), U2.45 (VDD), U2.55 (VDDDSI), U2.65 (VDDUSB), U2.77 (VDD), U2.100 (VDD), Y1.4 (VDD); also elsewhere on the board
/MCU/VDD12DSI: U2.56 (VCAPDSI), U2.62 (VDD12DSI)
/MCU/VDDA: C27.1, C51.1, C52.1, FB1.2, U2.17 (VREF+), U2.18 (VDDA)
CLK_RAM: R73.2, U2.81 (PC10)
CLR_DAC: U2.29 (PB0); also elsewhere on the board
GND: C27.2, C31.2, C32.2, C33.2, C34.2, C35.2, C36.2, C37.2, C38.2, C39.2, C40.2, C41.2, C42.2, C43.2, C44.2, C45.2, C46.1, C51.2, C52.2, C80.2, C81.2, IC5.4 (VSS), JP1.2 (B), JP2.2 (B), T_GND2.1, U2.2 (VSS), U2.7 (VSS), U2.16 (VSSA), U2.23 (VSS), U2.44 (VSS), U2.59 (VSSDSI), U2.78 (VSS), Y1.2 (GND); also elsewhere on the board
LED0: U2.98 (PB8); also elsewhere on the board
LED1: U2.99 (PB9); also elsewhere on the board
MISO_DAC: U2.27 (PA6); also elsewhere on the board
MISO_RAM: R72.1, U2.82 (PC11)
MOSI_DAC: U2.28 (PA7); also elsewhere on the board
MOSI_RAM: R74.2, U2.83 (PC12)
NRST: JP2.1 (A), U2.11 (NRST); also elsewhere on the board
NSS_DAC: U2.25 (PA4); also elsewhere on the board
NSS_RAM: IC5.1 (CE#), U2.80 (PA15)
unnamed: IC5.6 (CLK), R73.1
unnamed: IC5.5 (SI/SIO0), R74.1
unnamed: IC5.2 (SO/SIO1), R72.2
unnamed: JP1.1 (A), U2.97 (BOOT0)
unnamed: T_PC1.1, U2.13 (PC1)
unnamed: T_PC2.1, U2.14 (PC2)
unnamed: T_PC3.1, U2.15 (PC3)
unnamed: T_PE7.1, U2.32 (PE7)
unnamed: T_PE8.1, U2.33 (PE8)
unnamed: T_PE9.1, U2.34 (PE9)
unnamed: T_PE10.1, U2.35 (PE10)
unnamed: C31.1, U2.43 (VCAP1)
unnamed: C32.1, U2.76 (VCAP2)
OUT_UP_DAC: U2.30 (PB1); also elsewhere on the board
SCLK_DAC: U2.26 (PA5); also elsewhere on the board
SWCLK: U2.79 (PA14); also elsewhere on the board
SWDIO: U2.75 (PA13); also elsewhere on the board
SYS_CLK: U2.9 (PH0), Y1.3 (OUTPUT)
TR0_A: U2.19 (PA0); also elsewhere on the board
TR0_H: U2.84 (PD0); also elsewhere on the board
TR0_L: U2.85 (PD1); also elsewhere on the board
TR1_A: U2.20 (PA1); also elsewhere on the board
TR1_H: U2.87 (PD3); also elsewhere on the board
TR1_L: U2.88 (PD4); also elsewhere on the board
TR2_A: U2.21 (PA2); also elsewhere on the board
TR2_H: U2.91 (PD7); also elsewhere on the board
TR2_L: U2.50 (PD8); also elsewhere on the board
TR3_A: U2.22 (PA3); also elsewhere on the board
TR3_H: U2.52 (PD10); also elsewhere on the board
TR3_L: U2.53 (PD14); also elsewhere on the board
Trigger: U2.67 (PC7); also elsewhere on the board
USB_RX: T_RX1.1, U2.42 (PB11); also elsewhere on the board
USB_TX: T_TX1.1, U2.41 (PB10); also elsewhere on the board

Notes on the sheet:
Entkopplung
SRAM, 32Mbit
16 Mhz CLK

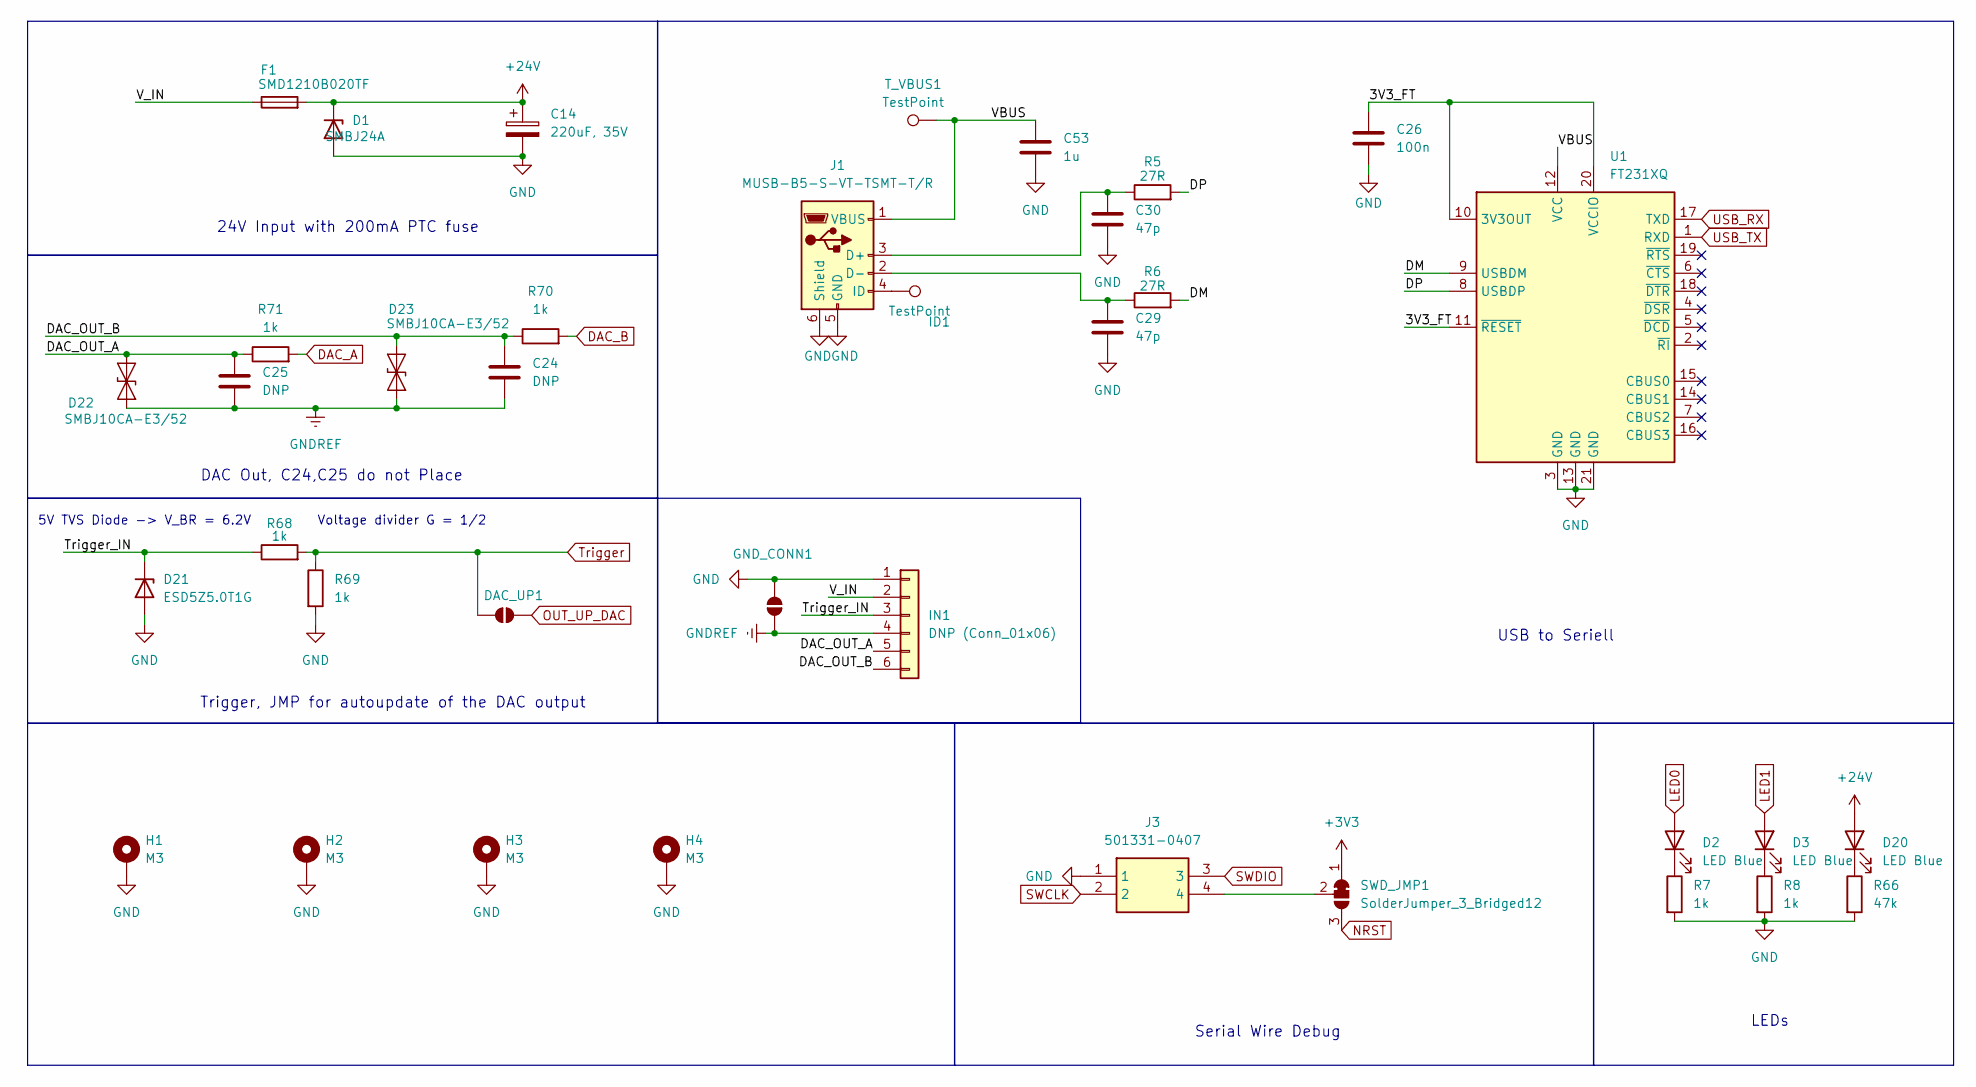
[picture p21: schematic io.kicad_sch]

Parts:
C14: 220uF, 35V; CP_Elec_8x10
C24, C25: DNP; C_0603_1608Metric
C26: 100n; C_0603_1608Metric
C29, C30: 47p; C_0603_1608Metric
C53: 1u; C_0603_1608Metric
D1: SMBJ24A; D_SMB
D2, D3, D20: LED Blue; LED_0603_1608Metric
D21: ESD5Z5.0T1G; D_SOD-523
D22, D23: SMBJ10CA-E3/52; D_SMB
DAC_UP1: SolderJumper_2_Open; SolderJumper-2_P1.3mm_Open_Pad1.0x1.5mm
F1: SMD1210B020TF; Fuse_1210_3225Metric
GND_CONN1: SolderJumper_2_Closed; SolderJumper-2_P1.3mm_Bridged_Pad1.0x1.5mm
H1, H2, H3, H4: M3; MountingHole_3.2mm_M3_Pad_Via
ID1: TestPoint; TestPoint_Pad_D1.5mm
IN1: DNP (Conn_01x06); PinHeader_1x06_P2.54mm_Vertical
J1: MUSB-B5-S-VT-TSMT-T/R; USB_Mini-B_AdamTech_MUSB-B5-S-VT-TSMT-1_SMD_Vertical
J3: 501331-0407; Mouser Part Number 538-501331-0407
R5, R6: 27R; R_0603_1608Metric
R7, R8, R68, R69, R70, R71: 1k; R_0603_1608Metric
R66: 47k; R_0603_1608Metric
SWD_JMP1: SolderJumper_3_Bridged12; SolderJumper-3_P1.3mm_Bridged12_RoundedPad1.0x1.5mm
T_VBUS1: TestPoint; TestPoint_Pad_D1.5mm
U1: FT231XQ; QFN-20-1EP_4x4mm_P0.5mm_EP2.5x2.5mm

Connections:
+3V3: SWD_JMP1.1 (A); also elsewhere on the board
+24V: C14.1, D1.1 (K), D20.2 (A), F1.2; also elsewhere on the board
/IO/3V3_FT: C26.1, U1.10 (3V3OUT), U1.11 (~RESET), U1.20 (VCCIO)
/IO/DAC_OUT_A: C25.1, D22.2 (A2), IN1.5, R71.1
/IO/DAC_OUT_B: C24.1, D23.2 (A2), IN1.6, R70.1
/IO/DM: R6.2, U1.9 (USBDM)
/IO/DP: R5.2, U1.8 (USBDP)
/IO/Trigger_IN: D21.1 (K), IN1.3, R68.1
/IO/VBUS: C53.1, J1.1 (VBUS), T_VBUS1.1, U1.12 (VCC)
/IO/V_IN: F1.1, IN1.2
DAC_A: R71.2; also elsewhere on the board
DAC_B: R70.2; also elsewhere on the board
GND: C14.2, C26.2, C29.2, C30.2, C53.2, D1.2 (A), D21.2 (A), GND_CONN1.2 (B), H1.MP, H2.MP, H3.MP, H4.MP, IN1.1, J1.5 (GND), J1.6 (Shield), J3.1, R7.2, R8.2, R66.2, R69.2, U1.3 (GND), U1.13 (GND), U1.21 (GND); also elsewhere on the board
GNDREF: C24.2, C25.2, D22.1 (A1), D23.1 (A1), GND_CONN1.1 (A), IN1.4; also elsewhere on the board
LED0: D2.2 (A); also elsewhere on the board
LED1: D3.2 (A); also elsewhere on the board
NRST: SWD_JMP1.3 (B); also elsewhere on the board
unnamed: D2.1 (K), R7.1
unnamed: D3.1 (K), R8.1
unnamed: D20.1 (K), R66.1
unnamed: C30.1, J1.3 (D+), R5.1
unnamed: C29.1, J1.2 (D-), R6.1
unnamed: ID1.1, J1.4 (ID)
unnamed: J3.4, SWD_JMP1.2 (C)
OUT_UP_DAC: DAC_UP1.2 (B); also elsewhere on the board
SWCLK: J3.2; also elsewhere on the board
SWDIO: J3.3; also elsewhere on the board
Trigger: DAC_UP1.1 (A), R68.2, R69.1; also elsewhere on the board
USB_RX: U1.17 (TXD); also elsewhere on the board
USB_TX: U1.1 (RXD); also elsewhere on the board

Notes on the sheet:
DAC Out, C24,C25 do not Place
24V Input with 200mA PTC fuse
LEDs
Trigger, JMP for autoupdate of the DAC output
Serial Wire Debug
USB to Seriell
5V TVS Diode -> V_BR = 6.2V
Voltage divider G = 1/2

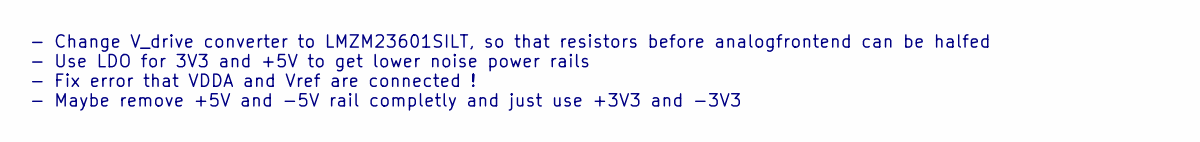
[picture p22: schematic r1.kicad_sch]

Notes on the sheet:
- Change V_drive converter to LMZM23601SILT, so that resistors before analogfrontend can be halfed - Use LDO for 3V3 and +5V to get lower noise power rails - Fix error that VDDA and Vref are connected ! - Maybe remove +5V and -5V rail completly and just use +3V3 and -3V3

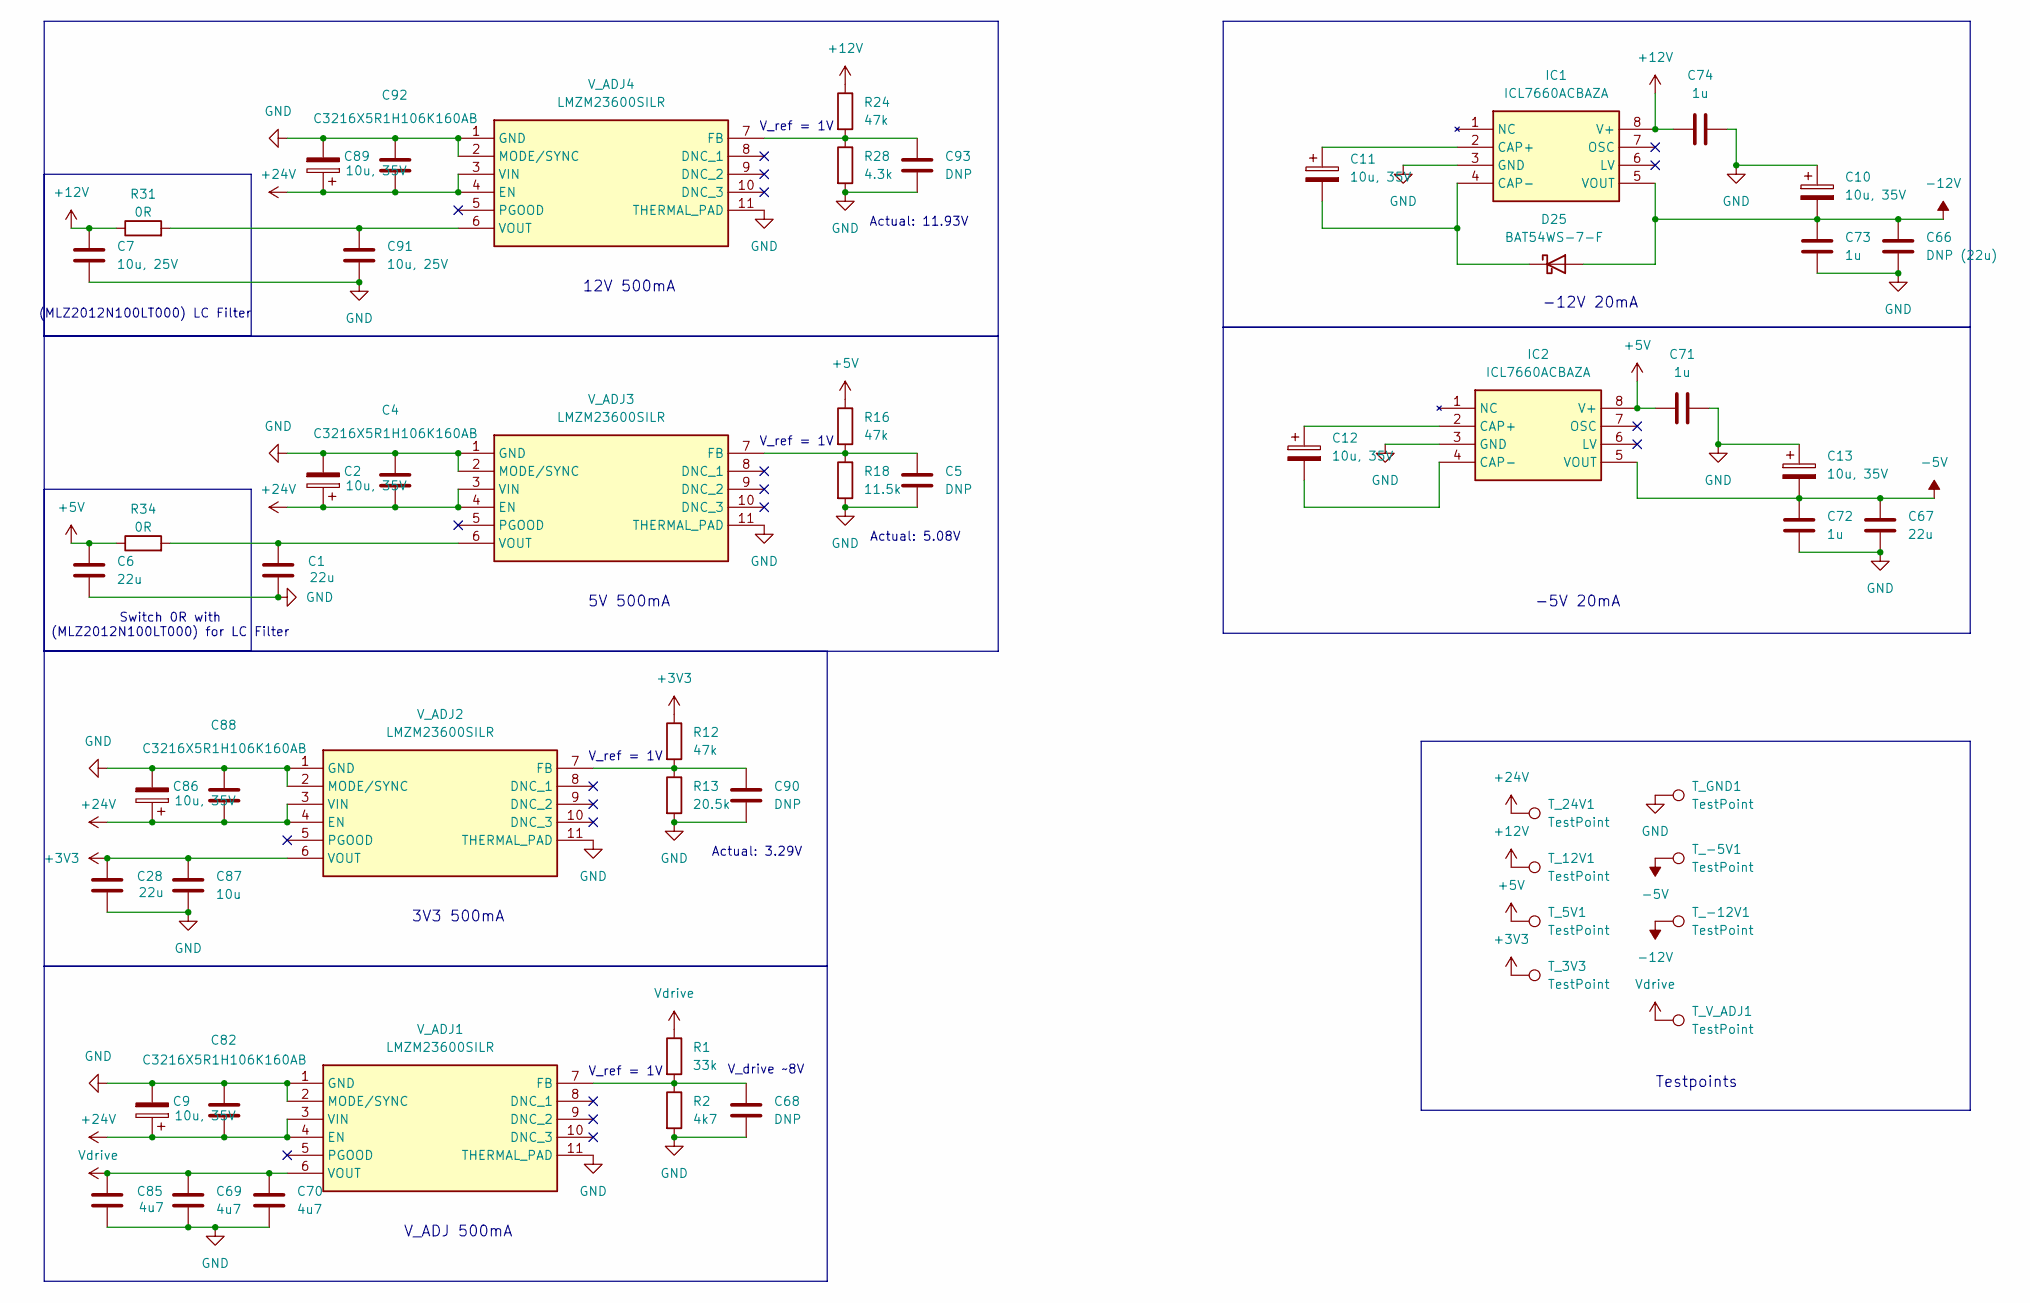
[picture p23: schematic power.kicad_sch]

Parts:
C1, C6, C28, C67: 22u; C_0805_2012Metric
C2, C9, C10, C11, C12, C13, C86, C89: 10u, 35V; CP_Elec_4x5.4
C4, C82, C88, C92: C3216X5R1H106K160AB; C_1206_3216Metric
C5, C68, C90, C93: DNP; C_0603_1608Metric
C7, C91: 10u, 25V; C_0805_2012Metric
C66: DNP (22u); C_0805_2012Metric
C69, C70, C85: 4u7; C_0805_2012Metric
C71, C72, C73, C74: 1u; C_0603_1608Metric
C87: 10u; C_0805_2012Metric
D25: BAT54WS-7-F; D_SOD-323
IC1, IC2: ICL7660ACBAZA; SOIC127P600X175-8N; Mouser Part Number 968-ICL7660CBAZA-T
R1: 33k; R_0603_1608Metric
R2: 4k7; R_0603_1608Metric
R12, R16, R24: 47k; R_0603_1608Metric
R13: 20.5k; R_0603_1608Metric
R18: 11.5k; R_0603_1608Metric
R28: 4.3k; R_0603_1608Metric
R31, R34: 0R; R_0805_2012Metric
T_3V3, T_5V1, T_12V1, T_24V1: TestPoint; TestPoint_Pad_D1.5mm
T_-5V1, T_-12V1: TestPoint; TestPoint_Pad_D1.5mm
T_GND1: TestPoint; TestPoint_Pad_D1.5mm
T_V_ADJ1: TestPoint; TestPoint_Pad_D1.5mm
V_ADJ1, V_ADJ2, V_ADJ3, V_ADJ4: LMZM23600SILR; LMZM23600SILT; Mouser Part Number 595-LMZM23600SILR

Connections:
+3V3: C28.1, C87.1, R12.1, T_3V3.1, V_ADJ2.6 (VOUT); also elsewhere on the board
+5V: C6.1, C71.2, IC2.8 (V+), R16.1, R34.1, T_5V1.1; also elsewhere on the board
+12V: C7.1, C74.1, IC1.8 (V+), R24.1, R31.1, T_12V1.1; also elsewhere on the board
+24V: C2.1, C4.2, C9.1, C82.2, C86.1, C88.2, C89.1, C92.2, T_24V1.1, V_ADJ1.3 (VIN), V_ADJ1.4 (EN), V_ADJ2.3 (VIN), V_ADJ2.4 (EN), V_ADJ3.3 (VIN), V_ADJ3.4 (EN), V_ADJ4.3 (VIN), V_ADJ4.4 (EN); also elsewhere on the board
-5V: C13.2, C67.1, C72.1, IC2.5 (VOUT), T_-5V1.1; also elsewhere on the board
-12V: C10.2, C66.1, C73.1, D25.2 (A), IC1.5 (VOUT), T_-12V1.1; also elsewhere on the board
GND: C1.2, C2.2, C4.1, C5.2, C6.2, C7.2, C9.2, C10.1, C13.1, C28.2, C66.2, C67.2, C68.2, C69.2, C70.2, C71.1, C72.2, C73.2, C74.2, C82.1, C85.2, C86.2, C87.2, C88.1, C89.2, C90.2, C91.2, C92.1, C93.2, IC1.3 (GND), IC2.3 (GND), R2.2, R13.2, R18.2, R28.2, T_GND1.1, V_ADJ1.1 (GND), V_ADJ1.2 (MODE/SYNC), V_ADJ1.11 (THERMAL_PAD), V_ADJ2.1 (GND), V_ADJ2.2 (MODE/SYNC), V_ADJ2.11 (THERMAL_PAD), V_ADJ3.1 (GND), V_ADJ3.2 (MODE/SYNC), V_ADJ3.11 (THERMAL_PAD), V_ADJ4.1 (GND), V_ADJ4.2 (MODE/SYNC), V_ADJ4.11 (THERMAL_PAD); also elsewhere on the board
unnamed: C11.2, D25.1 (K), IC1.4 (CAP-)
unnamed: C11.1, IC1.2 (CAP+)
unnamed: C12.1, IC2.2 (CAP+)
unnamed: C12.2, IC2.4 (CAP-)
unnamed: C68.1, R1.2, R2.1, V_ADJ1.7 (FB)
unnamed: C90.1, R12.2, R13.1, V_ADJ2.7 (FB)
unnamed: C5.1, R16.2, R18.1, V_ADJ3.7 (FB)
unnamed: C1.1, R34.2, V_ADJ3.6 (VOUT)
unnamed: C93.1, R24.2, R28.1, V_ADJ4.7 (FB)
unnamed: C91.1, R31.2, V_ADJ4.6 (VOUT)
Vdrive: C69.1, C70.1, C85.1, R1.1, T_V_ADJ1.1, V_ADJ1.6 (VOUT); also elsewhere on the board

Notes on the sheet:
V_ref = 1V
-5V 20mA
V_drive ~8V
Actual: 5.08V
Switch 0R with (MLZ2012N100LT000) for LC Filter
3V3 500mA
Actual: 11.93V
(MLZ2012N100LT000) LC Filter
5V 500mA
Actual: 3.29V
Testpoints
-12V 20mA
12V 500mA
V_ADJ 500mA

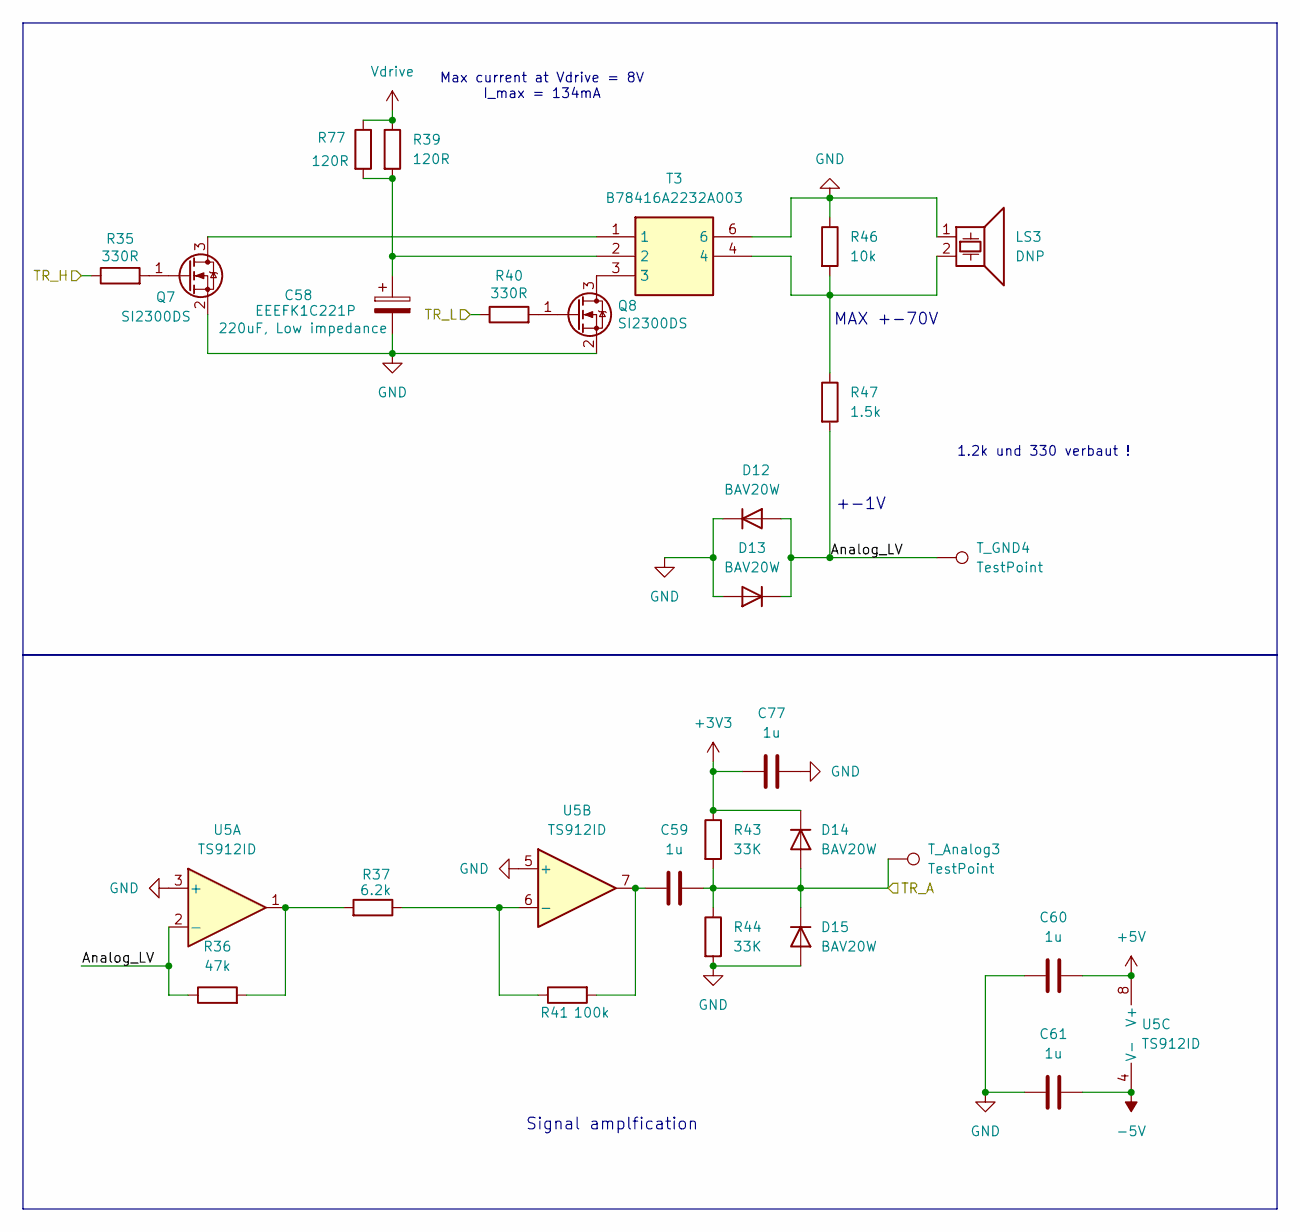
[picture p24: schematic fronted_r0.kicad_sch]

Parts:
C58: EEEFK1C221P; CP_Elec_8x6.2
C59, C60, C61, C77: 1u; C_0603_1608Metric
D12, D13, D14, D15: BAV20W; D_SOD-123
LS3: DNP; US_Solderpad
Q7, Q8: SI2300DS; SOT-23-3
R35, R40: 330R; R_0603_1608Metric
R36: 47k; R_0603_1608Metric
R37: 6.2k; R_0603_1608Metric
R39, R77: 120R; R_0603_1608Metric
R41: 100k; R_0603_1608Metric
R43, R44: 33K; R_0603_1608Metric
R46: 10k; R_0603_1608Metric
R47: 1.5k; R_0603_1608Metric
T3: B78416A2232A003; Mouser Part Number 871-B78416A2232A003
T_Analog3: TestPoint; TestPoint_Pad_D1.5mm
T_GND4: TestPoint; TestPoint_Pad_D1.5mm
U5: TS912ID; SOIC-8_3.9x4.9mm_P1.27mm

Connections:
+3V3: C77.1, D14.1 (K), R43.1; also elsewhere on the board
+5V: C60.2, U5.8 (V+); also elsewhere on the board
-5V: C61.2, U5.4 (V-); also elsewhere on the board
/Analog/frontend_2/Analog_LV: D12.2 (A), D13.1 (K), R36.1, R47.2, T_GND4.1, U5.2 (-)
GND: C58.2, C60.1, C61.1, C77.2, D12.1 (K), D13.2 (A), D15.2 (A), LS3.1, Q7.2 (S), Q8.2 (S), R44.2, R46.1, T3.6, U5.3 (+), U5.5 (+); also elsewhere on the board
unnamed: C58.1, R39.2, R77.2, T3.2
unnamed: C59.1, R41.2, U5.7
unnamed: LS3.2, R46.2, R47.1, T3.4
unnamed: Q7.3 (D), T3.1
unnamed: Q7.1 (G), R35.2
unnamed: Q8.3 (D), T3.3
unnamed: Q8.1 (G), R40.2
unnamed: R36.2, R37.2, U5.1
unnamed: R37.1, R41.1, U5.6 (-)
TR2_A: C59.2, D14.2 (A), D15.1 (K), R43.2, R44.1, T_Analog3.1; also elsewhere on the board
TR2_H: R35.1; also elsewhere on the board
TR2_L: R40.1; also elsewhere on the board
Vdrive: R39.1, R77.1; also elsewhere on the board

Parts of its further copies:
C47, C49, C50, C55, C56, C57, C63, C64, C65, C75, C76, C78: 1u; C_0603_1608Metric
C48, C54, C62: EEEFK1C221P; CP_Elec_8x6.2
D4, D5, D6, D7, D8, D9, D10, D11, D16, D17, D18, D19: BAV20W; D_SOD-123
LS1, LS2, LS4: DNP; US_Solderpad
Q1, Q2, Q4, Q5, Q10, Q11: SI2300DS; SOT-23-3
R3, R25, R53, R75, R76, R78: 120R; R_0603_1608Metric
R4, R9, R21, R26, R49, R54: 330R; R_0603_1608Metric
R10, R32, R60: 10k; R_0603_1608Metric
R11, R33, R61: 1.5k; R_0603_1608Metric
R14, R22, R50: 47k; R_0603_1608Metric
R15, R23, R51: 6.2k; R_0603_1608Metric
R17, R27, R55: 100k; R_0603_1608Metric
R19, R20, R29, R30, R57, R58: 33K; R_0603_1608Metric
T1, T2, T4: B78416A2232A003; Mouser Part Number 871-B78416A2232A003
T_Analog1, T_Analog2, T_Analog4: TestPoint; TestPoint_Pad_D1.5mm
T_GND3, T_GND5: TestPoint; TestPoint_Pad_D1.5mm
T_TR_A1: TestPoint; TestPoint_Pad_D1.5mm
U3, U4, U6: TS912ID; SOIC-8_3.9x4.9mm_P1.27mm

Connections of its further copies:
+3V3: C75.1, C76.1, C78.1, D6.1 (K), D10.1 (K), D18.1 (K), R20.1, R29.1, R57.1; also elsewhere on the board
+5V: C47.2, C56.2, C64.2, U3.8 (V+), U4.8 (V+), U6.8 (V+); also elsewhere on the board
-5V: C49.2, C57.2, C65.2, U3.4 (V-), U4.4 (V-), U6.4 (V-); also elsewhere on the board
/Analog/frontend_0/Analog_LV: D4.2 (A), D5.1 (K), R11.2, R14.1, T_Analog1.1, U3.2 (-)
/Analog/frontend_1/Analog_LV: D8.2 (A), D9.1 (K), R22.1, R33.2, T_GND3.1, U4.2 (-)
/Analog/frontend_3/Analog_LV: D16.2 (A), D17.1 (K), R50.1, R61.2, T_GND5.1, U6.2 (-)
GND: C47.1, C48.2, C49.1, C54.2, C56.1, C57.1, C62.2, C64.1, C65.1, C75.2, C76.2, C78.2, D4.1 (K), D5.2 (A), D7.2 (A), D8.1 (K), D9.2 (A), D11.2 (A), D16.1 (K), D17.2 (A), D19.2 (A), LS1.1, LS2.1, LS4.1, Q1.2 (S), Q2.2 (S), Q4.2 (S), Q5.2 (S), Q10.2 (S), Q11.2 (S), R10.1, R19.2, R30.2, R32.1, R58.2, R60.1, T1.6, T2.6, T4.6, U3.3 (+), U3.5 (+), U4.3 (+), U4.5 (+), U6.3 (+), U6.5 (+); also elsewhere on the board
unnamed: C48.1, R3.2, R75.2, T1.2
unnamed: C50.1, R17.2, U3.7
unnamed: C54.1, R25.2, R76.2, T2.2
unnamed: C55.1, R27.2, U4.7
unnamed: C62.1, R53.2, R78.2, T4.2
unnamed: C63.1, R55.2, U6.7
unnamed: LS1.2, R10.2, R11.1, T1.4
unnamed: LS2.2, R32.2, R33.1, T2.4
unnamed: LS4.2, R60.2, R61.1, T4.4
unnamed: Q1.3 (D), T1.1
unnamed: Q1.1 (G), R4.2
unnamed: Q2.3 (D), T1.3
unnamed: Q2.1 (G), R9.2
unnamed: Q4.3 (D), T2.1
unnamed: Q4.1 (G), R21.2
unnamed: Q5.3 (D), T2.3
unnamed: Q5.1 (G), R26.2
unnamed: Q10.3 (D), T4.1
unnamed: Q10.1 (G), R49.2
unnamed: Q11.3 (D), T4.3
unnamed: Q11.1 (G), R54.2
unnamed: R14.2, R15.2, U3.1
unnamed: R22.2, R23.2, U4.1
unnamed: R50.2, R51.2, U6.1
unnamed: R15.1, R17.1, U3.6 (-)
unnamed: R23.1, R27.1, U4.6 (-)
unnamed: R51.1, R55.1, U6.6 (-)
TR0_A: C50.2, D6.2 (A), D7.1 (K), R19.1, R20.2, T_TR_A1.1; also elsewhere on the board
TR0_H: R4.1; also elsewhere on the board
TR0_L: R9.1; also elsewhere on the board
TR1_A: C55.2, D10.2 (A), D11.1 (K), R29.2, R30.1, T_Analog2.1; also elsewhere on the board
TR1_H: R21.1; also elsewhere on the board
TR1_L: R26.1; also elsewhere on the board
TR3_A: C63.2, D18.2 (A), D19.1 (K), R57.2, R58.1, T_Analog4.1; also elsewhere on the board
TR3_H: R49.1; also elsewhere on the board
TR3_L: R54.1; also elsewhere on the board
Vdrive: R3.1, R25.1, R53.1, R75.1, R76.1, R78.1; also elsewhere on the board

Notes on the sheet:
MAX +-70V
+-1V
1.2k und 330 verbaut !
Max current at Vdrive = 8V I_max = 134mA
Signal amplfication

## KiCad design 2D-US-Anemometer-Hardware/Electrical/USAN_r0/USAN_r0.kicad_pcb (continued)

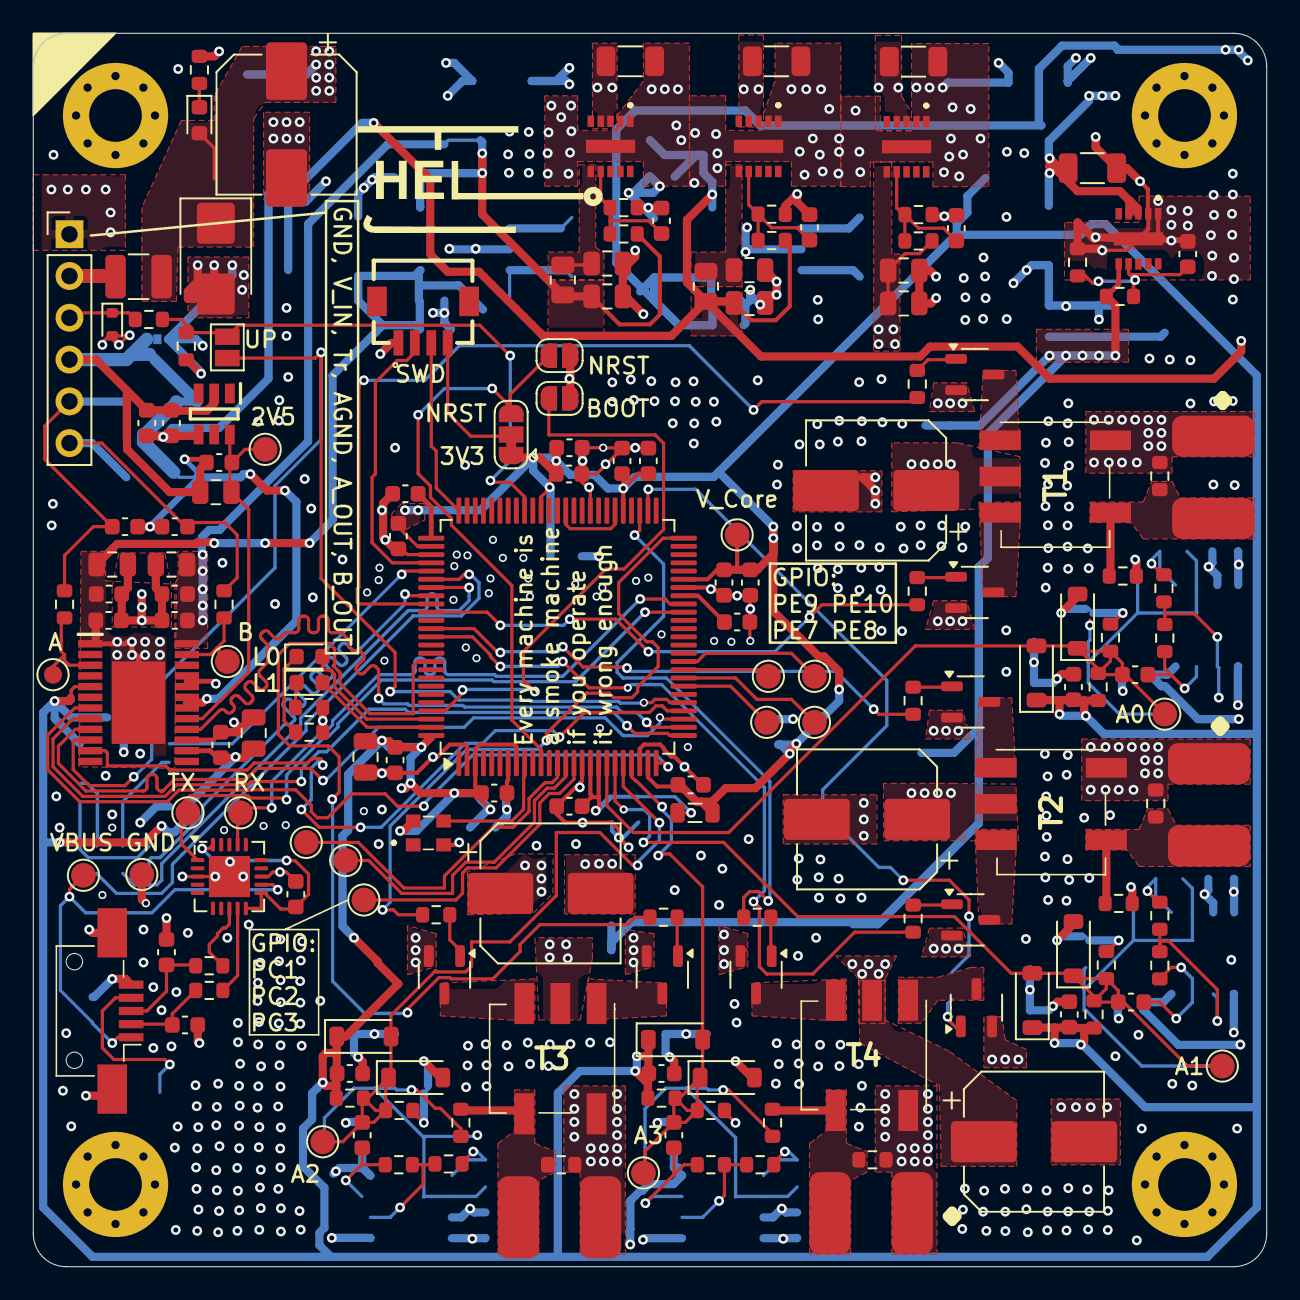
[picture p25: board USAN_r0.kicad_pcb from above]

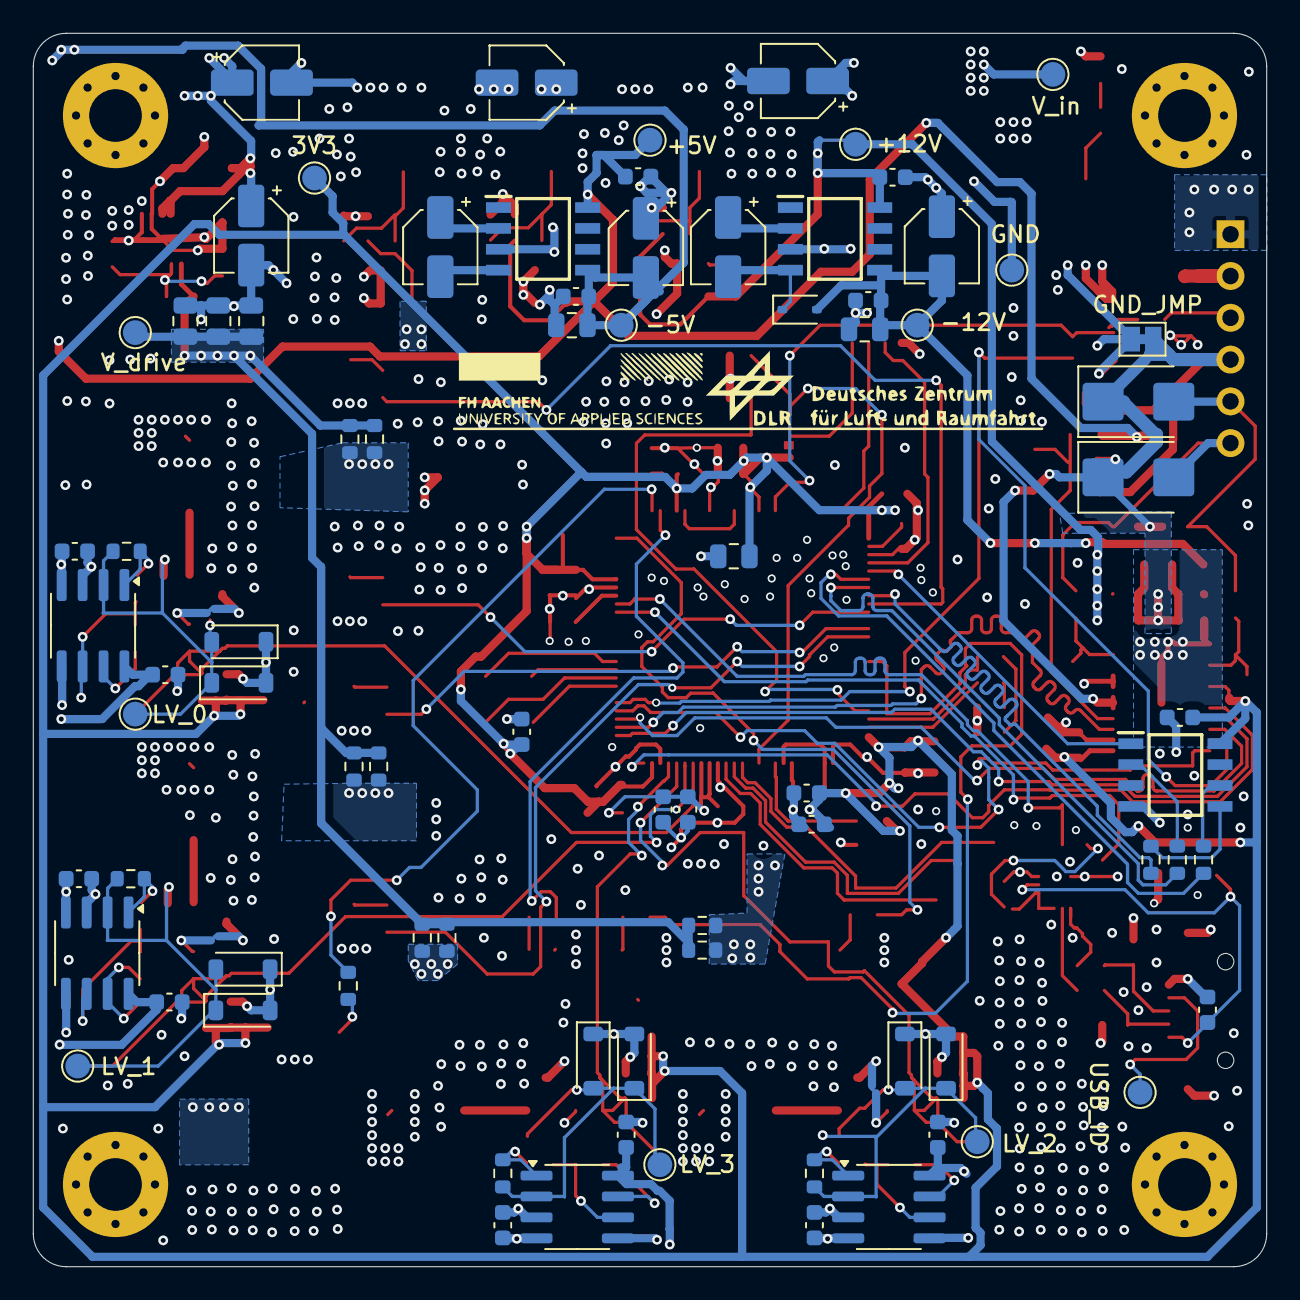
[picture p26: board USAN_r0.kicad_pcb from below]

Board: 4 copper layers, 75.0 x 75.0 mm, 259 parts (81 on the bottom side), 123 nets.

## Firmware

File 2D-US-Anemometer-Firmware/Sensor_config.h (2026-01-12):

/*
Copyright 2025 Till Weise

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
1. Redistributions of source code must retain the above copyright notice,
 this list of conditions and the following disclaimer.

2. Redistributions in binary form must reproduce the above copyright notice,
 this list of conditions and the following disclaimer in the documentation and/or other materials provided with the distribution.

3. Neither the name of the copyright holder nor the names of its contributors may be used to endorse or promote products
 derived from this software without specific prior written permission.

THIS SOFTWARE IS PROVIDED BY THE COPYRIGHT HOLDERS AND CONTRIBUTORS “AS IS” AND ANY EXPRESS OR IMPLIED WARRANTIES, INCLUDING,
 BUT NOT LIMITED TO, THE IMPLIED WARRANTIES OF MERCHANTABILITY AND FITNESS FOR A PARTICULAR PURPOSE ARE DISCLAIMED.
 IN NO EVENT SHALL THE COPYRIGHT HOLDER OR CONTRIBUTORS BE LIABLE FOR ANY DIRECT, INDIRECT, INCIDENTAL, SPECIAL, EXEMPLARY,
 OR CONSEQUENTIAL DAMAGES (INCLUDING, BUT NOT LIMITED TO, PROCUREMENT OF SUBSTITUTE GOODS OR SERVICES; LOSS OF USE, DATA, OR PROFITS;
 OR BUSINESS INTERRUPTION) HOWEVER CAUSED AND ON ANY THEORY OF LIABILITY, WHETHER IN CONTRACT, STRICT LIABILITY,
 OR TORT (INCLUDING NEGLIGENCE OR OTHERWISE) ARISING IN ANY WAY OUT OF THE USE OF THIS SOFTWARE,
 EVEN IF ADVISED OF THE POSSIBILITY OF SUCH DAMAGE.
*/



#define d_0 0.0632 //Geom length of the measurement path
//if the length is changed the ADC offset has to be changed the fomular is as follows
//        (d_0/343)/(1/SHOT_FREQ) - 20 
#define ADC_OFFSET 120

#define SUB_MEASUREMENT_FREQ 200 //Up to 250Hz
#define CLOCK_MARGINE 0 // in us -> increase if clock drift is to large

//Key  and Calibration
#define ZERO_MEAS_SAMPLES 50 // Number of samples of the zero meas while testing 
//#define KEY_TEST // activates the KEY test part of the programm
#define KEY_DEFAULT 1926 //1814-> key for 14mm TR //1926 -> Key for 10mm TR //Here goes the chosen key of the test
#define CALIB_SAMPLES 600 // count of samples over which is averaged, for Calibration
#define VALID_SAMPLES 5 // count of samples over which is averaged, for  Validation

// Meas Paramter
#define MEASUREMENT_INTER_ERROR_CALIBRATION 10.0    //Allowed velocity diviation from mean, until sample is discarded, at calibration
#define MEASUREMENT_INTER_ERROR 25.0                //Allowed velocity diviation from mean, until sample is discarded, at normal meas
//#define EXPERIMENTAL_HIGH_SPEED_PEAK_SELCTION 0.01  //Allows the Algorithem to choose a peak based on feasbilty if blow threshhold, comment out to deactivate

// AXIS settings, changes are applied in this order!
#define SWAP_AXIS false // Swaps the X and Y outputs of the sensor
#define INVERT_X false // Invert X-axis
#define INVERT_Y true // Invert Y-axis

//#define PYTHON_INTERFACE  1

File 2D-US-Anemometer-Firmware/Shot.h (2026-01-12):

/*
Copyright 2025 Till Weise

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
1. Redistributions of source code must retain the above copyright notice,
 this list of conditions and the following disclaimer.

2. Redistributions in binary form must reproduce the above copyright notice,
 this list of conditions and the following disclaimer in the documentation and/or other materials provided with the distribution.

3. Neither the name of the copyright holder nor the names of its contributors may be used to endorse or promote products
 derived from this software without specific prior written permission.

THIS SOFTWARE IS PROVIDED BY THE COPYRIGHT HOLDERS AND CONTRIBUTORS “AS IS” AND ANY EXPRESS OR IMPLIED WARRANTIES, INCLUDING,
 BUT NOT LIMITED TO, THE IMPLIED WARRANTIES OF MERCHANTABILITY AND FITNESS FOR A PARTICULAR PURPOSE ARE DISCLAIMED.
 IN NO EVENT SHALL THE COPYRIGHT HOLDER OR CONTRIBUTORS BE LIABLE FOR ANY DIRECT, INDIRECT, INCIDENTAL, SPECIAL, EXEMPLARY,
 OR CONSEQUENTIAL DAMAGES (INCLUDING, BUT NOT LIMITED TO, PROCUREMENT OF SUBSTITUTE GOODS OR SERVICES; LOSS OF USE, DATA, OR PROFITS;
 OR BUSINESS INTERRUPTION) HOWEVER CAUSED AND ON ANY THEORY OF LIABILITY, WHETHER IN CONTRACT, STRICT LIABILITY,
 OR TORT (INCLUDING NEGLIGENCE OR OTHERWISE) ARISING IN ANY WAY OUT OF THE USE OF THIS SOFTWARE,
 EVEN IF ADVISED OF THE POSSIBILITY OF SUCH DAMAGE.
*/
#pragma once

#include "main.h"
#include "stdlib.h" 
#include "gpio.h"
#include "stm32f4xx_hal.h"
#include "stm32f4xx_hal_dma.h"
#include "stm32f4xx_hal_adc.h"
#include "Sensor_config.h"
#include <math.h>

#define SHOT_KEY_LENGTH 12
#define SHOT_DMA_CYCLES_PER_PERIODE 20
#define SHOT_DMA_LENGTH  512 
#define SHOT_FREQ 800000
#define SHOT_ADC_OFFSET ADC_OFFSET

#define SHOT_PORT GPIOD
//Transceiver 0
#define SHOT_TR0_H GPIO_PIN_0
#define SHOT_TR0_L GPIO_PIN_1
#define SHOT_TR0_C GPIO_PIN_2
#define SHOT_TR0_A ADC_CHANNEL_0

//Transceiver 1
#define SHOT_TR1_H GPIO_PIN_3
#define SHOT_TR1_L GPIO_PIN_4
#define SHOT_TR1_C GPIO_PIN_5
#define SHOT_TR1_A ADC_CHANNEL_1

//Transceiver 2
#define SHOT_TR2_H GPIO_PIN_7
#define SHOT_TR2_L GPIO_PIN_8
#define SHOT_TR2_C GPIO_PIN_9
#define SHOT_TR2_A ADC_CHANNEL_2

//Transceiver 3
#define SHOT_TR3_H GPIO_PIN_10
#define SHOT_TR3_L GPIO_PIN_14
#define SHOT_TR3_C GPIO_PIN_15
#define SHOT_TR3_A ADC_CHANNEL_3

//Modulo for fire squence 
#define SHOT_POW_MODULO 2

typedef struct{
  uint16_t TR_H;  //Highside of Transmitter
  uint16_t TR_L;  //Lowside of Transmitter
  uint16_t TR_C;  //F-FETs that have to be deactivate for send and receive 
  uint16_t TR_CC; //  ->For Dampening after Sending
  uint32_t TR_A;  //Analog of receiver
  uint16_t gpio_data[SHOT_DMA_LENGTH];
}Transceiver_handle;

typedef struct{
uint8_t lock; //0 Open , 1 Locked do not touch 
uint16_t data[SHOT_DMA_LENGTH + SHOT_ADC_OFFSET];
}Shot_data_struct;


/**
  GPIO, ADC, DMA, Tim set up 
*/
uint8_t Shot_Init(Transceiver_handle* handle);

/**
  Generates GPIO register states from KEY for usage with DMA
  handle is must be array of 4
*/
uint8_t Shot_generate_gpio_from_Key(uint8_t *KEY, Transceiver_handle *handle);

//Alternativ ways to generate the KEY, sometimes very interesting results
uint8_t Shot_generate_gpio_from_Key_2(uint8_t *KEY, Transceiver_handle *handle);
uint8_t Shot_generate_gpio_from_Key_3(uint8_t *KEY, Transceiver_handle *handle);
uint8_t Shot_generate_gpio_from_Key_4(uint8_t *KEY, Transceiver_handle *handle);

/**
  Fire in the hole 
  Data has to be Unlocked after DMA is finnished 
*/
uint8_t Shot_fire(Transceiver_handle *handle, Shot_data_struct *data);

/**
  Unlocks data struct if Shot is finshed
*/
uint8_t Shot_unlock_data(Shot_data_struct * data);

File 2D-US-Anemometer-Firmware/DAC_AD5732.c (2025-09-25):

/*
Copyright 2025 Till Weise

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
1. Redistributions of source code must retain the above copyright notice,
 this list of conditions and the following disclaimer.

2. Redistributions in binary form must reproduce the above copyright notice,
 this list of conditions and the following disclaimer in the documentation and/or other materials provided with the distribution.

3. Neither the name of the copyright holder nor the names of its contributors may be used to endorse or promote products
 derived from this software without specific prior written permission.

THIS SOFTWARE IS PROVIDED BY THE COPYRIGHT HOLDERS AND CONTRIBUTORS “AS IS” AND ANY EXPRESS OR IMPLIED WARRANTIES, INCLUDING,
 BUT NOT LIMITED TO, THE IMPLIED WARRANTIES OF MERCHANTABILITY AND FITNESS FOR A PARTICULAR PURPOSE ARE DISCLAIMED.
 IN NO EVENT SHALL THE COPYRIGHT HOLDER OR CONTRIBUTORS BE LIABLE FOR ANY DIRECT, INDIRECT, INCIDENTAL, SPECIAL, EXEMPLARY,
 OR CONSEQUENTIAL DAMAGES (INCLUDING, BUT NOT LIMITED TO, PROCUREMENT OF SUBSTITUTE GOODS OR SERVICES; LOSS OF USE, DATA, OR PROFITS;
 OR BUSINESS INTERRUPTION) HOWEVER CAUSED AND ON ANY THEORY OF LIABILITY, WHETHER IN CONTRACT, STRICT LIABILITY,
 OR TORT (INCLUDING NEGLIGENCE OR OTHERWISE) ARISING IN ANY WAY OUT OF THE USE OF THIS SOFTWARE,
 EVEN IF ADVISED OF THE POSSIBILITY OF SUCH DAMAGE.
*/
#include "main.h"
#include "stdlib.h"
#include "DAC_AD5732.h"
#include "gpio.h"
#include "Shared.h"

//Register Definitions
#define REG_DAC      0b00000000
#define REG_RANGE    0b00001000
#define REG_PW       0b00010000
#define REG_CON      0b00011000
#define REG_READ     0b10000000
#define REG_WRITE    0b00000000
#define REG_NOP      0b00011000


#define RANGE_u_5    0b00000000 // Unipolar
#define RANGE_u_10   0b00000001
#define RANGE_u_10_8 0b00000010
#define RANGE_b_5    0b00000011 // Bipolar
#define RANGE_b_10   0b00000100
#define RANGE_b_10_8 0b00000101

#define ADDR_A       0b00000000
#define ADDR_B       0b00000010
#define ADDR_AB      0b00000100

#define PW_UP_AB     0b00000101
  

#define Volt_to_cnt (DAC_V_RANGE / 16384.0)
#define V_max DAC_V_RANGE / DAC_V_TYPE - DAC_V_MARGIN
#define V_min (-DAC_V_RANGE *(DAC_V_TYPE - 1)) / DAC_V_TYPE + DAC_V_MARGIN



SPI_HandleTypeDef DAC_SPI_HANDLE;
SPI_HandleTypeDef hspi1;

/*
 * Extern
 */
uint8_t DAC_Init();
uint8_t DAC_write(float V_A, float V_B, uint8_t Update);

/*
 * Intern
 */
uint16_t DAC_Volt_to_CNT_A(float V_in);
uint16_t DAC_Volt_to_CNT_B(float V_in);

// GPIO Data struct
gpio_pin_init_t gpio_pin_NSS, gpio_pin_Clear, gpio_pin_UP;




uint8_t DAC_Init(){
  // Starting SPI
  hspi1.Instance = SPI1;
  hspi1.Init.Mode = SPI_MODE_MASTER;
  hspi1.Init.Direction = SPI_DIRECTION_2LINES;
  hspi1.Init.DataSize = SPI_DATASIZE_8BIT;
  hspi1.Init.CLKPolarity = SPI_POLARITY_LOW;
  hspi1.Init.CLKPhase = SPI_PHASE_1EDGE;
  hspi1.Init.NSS = SPI_NSS_SOFT;
  hspi1.Init.BaudRatePrescaler = SPI_BAUDRATEPRESCALER_4;
  hspi1.Init.FirstBit = SPI_FIRSTBIT_MSB;
  hspi1.Init.TIMode = SPI_TIMODE_DISABLE;
  hspi1.Init.CRCCalculation = SPI_CRCCALCULATION_DISABLE;
  hspi1.Init.CRCPolynomial = 10;
  if (HAL_SPI_Init(&hspi1) != HAL_OK) {
    Error_Handler(2);
  }

  // Init Pins
  gpio_pin_NSS.pin.num = DAC_NSS_PIN;
  gpio_pin_NSS.pin.bank = DAC_NSS_PORT;
  gpio_pin_NSS.mode = OUTPUT_PUSH_PULL;
  gpio_pin_NSS.pull = PULL_NONE;
  gpio_pin_NSS.speed = SPEED_HIGH;

  gpio_pin_Clear.pin.num = DAC_CLEAR_PIN;
  gpio_pin_Clear.pin.bank = DAC_CLEAR_PORT;
  gpio_pin_Clear.mode = OUTPUT_PUSH_PULL;
  gpio_pin_Clear.pull = PULL_NONE;
  gpio_pin_Clear.speed = SPEED_HIGH;

  gpio_pin_UP.pin.num = DAC_UP_PIN;
  gpio_pin_UP.pin.bank = DAC_UP_PORT;
  gpio_pin_UP.mode = OUTPUT_PUSH_PULL;
  gpio_pin_UP.pull = PULL_NONE;
  gpio_pin_UP.speed = SPEED_HIGH;
  gpio_pin_init(&gpio_pin_NSS);
  gpio_pin_init(&gpio_pin_Clear);
  gpio_pin_init(&gpio_pin_UP);

  gpio_pin_write(gpio_pin_NSS.pin, 1);
  gpio_pin_write(gpio_pin_UP.pin, 1);
  gpio_pin_write(gpio_pin_Clear.pin,1);

  // Set Range
  uint8_t MSG[3] = {0};
  MSG[0] = MSG[0] | REG_WRITE | REG_RANGE | ADDR_AB;
  MSG[2] = MSG[2] | DAC_USE_RANGE;

  gpio_pin_write(gpio_pin_NSS.pin, 0);
    __NOP(); //Empty instruction
  HAL_SPI_Transmit(&DAC_SPI_HANDLE, &MSG[0], 1, 10);
  HAL_SPI_Transmit(&DAC_SPI_HANDLE, &MSG[1], 1, 10);
  HAL_SPI_Transmit(&DAC_SPI_HANDLE, &MSG[2], 1, 10);
  gpio_pin_write(gpio_pin_NSS.pin, 1);
  HAL_Delay(10);

  // Power up channels
  MSG[0] = 0 | REG_WRITE | REG_PW;
  MSG[1] = 0;
  MSG[2] = 0 | PW_UP_AB;

  gpio_pin_write(gpio_pin_NSS.pin, 0);
  __NOP(); //Empty instruction so register is updated
  HAL_SPI_Transmit(&DAC_SPI_HANDLE, &MSG[0], 1, 10);
  HAL_SPI_Transmit(&DAC_SPI_HANDLE, &MSG[1], 1, 10);
  HAL_SPI_Transmit(&DAC_SPI_HANDLE, &MSG[2], 1, 10);
  gpio_pin_write(gpio_pin_NSS.pin, 1);
  HAL_Delay(10);

  return EXIT_SUCCESS;
}

uint8_t DAC_write(float V_A, float V_B, uint8_t Update){
	if(V_A > V_max | V_A < V_min | V_B > V_max | V_B < V_min){ //Checking Input
		return EXIT_FAILURE;
	}

        //Shifting data in to Format
	uint16_t A_cnt = DAC_Volt_to_CNT_A(V_A);
	uint16_t B_cnt = DAC_Volt_to_CNT_B(V_B);

        //Writing OUT A Register
	uint8_t MSG_A[3] = {0};
	uint16_t *ptr =(uint16_t*)&MSG_A[1];
	MSG_A[0] = REG_DAC | ADDR_A;
        MSG_A[1] = (A_cnt >> 8) & 0x00FF;
        MSG_A[2] = (A_cnt) & 0x00FF;

        gpio_pin_write(gpio_pin_NSS.pin,0);
        __NOP();
       	HAL_SPI_Transmit(&DAC_SPI_HANDLE, MSG_A, 3, 10);
	gpio_pin_write(gpio_pin_NSS.pin,1);



        //Writing OUT B Register
	uint8_t MSG_B[3] = {0};
	ptr =(uint16_t*)&MSG_B[1];
	MSG_B[0] = REG_WRITE | REG_DAC | ADDR_B;
        MSG_B[1] = (B_cnt >> 8) & 0x00FF;
        MSG_B[2] = (B_cnt) & 0x00FF;

	gpio_pin_write(gpio_pin_NSS.pin,0);
        __NOP();
	HAL_SPI_Transmit(&DAC_SPI_HANDLE, MSG_B, 3, 10);
	gpio_pin_write(gpio_pin_NSS.pin,1);


	if(Update == 1){ //Trigger update PIN
		gpio_pin_write(gpio_pin_UP.pin,0);
                // Wait for the register to be written 
                __NOP();
                __NOP();
                __NOP();
		gpio_pin_write(gpio_pin_UP.pin,1);

	}
	return EXIT_SUCCESS;
}


uint16_t DAC_Volt_to_CNT_A(float V_in){
	//Future space for Calibration

	 uint16_t ret = 0b0010000000000000; //Offset for 0 V,, 2 bit shifted
         float h1 = (1.0/Volt_to_cnt);
         float h2 = V_in * h1;
         int16_t h3 = (int16_t)h2;
         ret = ret + h3;
 
	 return ret << 2; // Shift by to bit see datasheet
}
uint16_t DAC_Volt_to_CNT_B(float V_in){
	//Future space for Calibration

	 uint16_t ret = 0b0010000000000000; //Offset for 0 V,, 2 bit shifted
         float h1 = (1.0/Volt_to_cnt);
         float h2 = V_in * h1;
         int16_t h3 = (int16_t)h2;
         ret = ret + h3;
 
	 return ret << 2; // Shift by to bit see datasheet
}

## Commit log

2025-09-25 Add CAD and KiCAD
    [501331-0407.0001.iam, 501331-0407.iam, 5013310407.0001.ipt, 5013310407.ipt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]
2025-09-26 add CAD parts
    [Lid.stp, Solder_aid.ipt, Solder_aid.stl, Solder_aid.stp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]
